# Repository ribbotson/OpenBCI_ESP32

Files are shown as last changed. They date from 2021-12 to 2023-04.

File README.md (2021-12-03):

# OpenBCI_ESP32
Clone of OpenBCI Brain Computer Interface Hardware using ESP32 Processor

>OpenBCI Cyton is a well performing Open source hardware and software design for a Brain Computer Interface. It was designed and developed over the last 7 years and used in many experimants and applications.
>This clone is designed because some of the parts used in the Cyton hardware are now obsolete and difficult to source. Also it is hoped that a new design can offer higher throughput. 
The design will continue to use the TI ADS1299 Analog Front end so perfomance should be the same as Cyton. The option to have either 8 or 16 channels will be retained.

## Changes for ESP Version

**Replace existing PIC32MX processor with ESP32 processor with integral WiFi and Bluetooth**

>The ESP32 was chosen because it has integral WiFi and bluetooth and so replaces the obsolete RFD22301 bluetooth module and the WiFi board. The ESP32 is better supported under Arduino environment than PIC and RFD device. Raspberry Pi Zero W was considered as it has more processing power, but was excluded due to much higher power consumption so not suitable for battery operation.

**The design is split into two plugable modules**

>The base module supports the Processor, Micro SD Card, Accelerometer, and Power Supplies. One or two input modules are the stacked below to add 8 or 16 electrode inputs. The first base module will use a prebuilt ESP32 DEVkit C module to make firmware development easier. A later version could place as smaller ESP32 module directly on the base module.

**Boards only have components on one side**

>To simplify construction the new boards only have components mounted on one side of the board. Both boards are 2 layer PCB.

**Some components are to allow use of more common generic devices**

>Use of more common generic components should help with procurement especially if using outsourced PCB Assembly

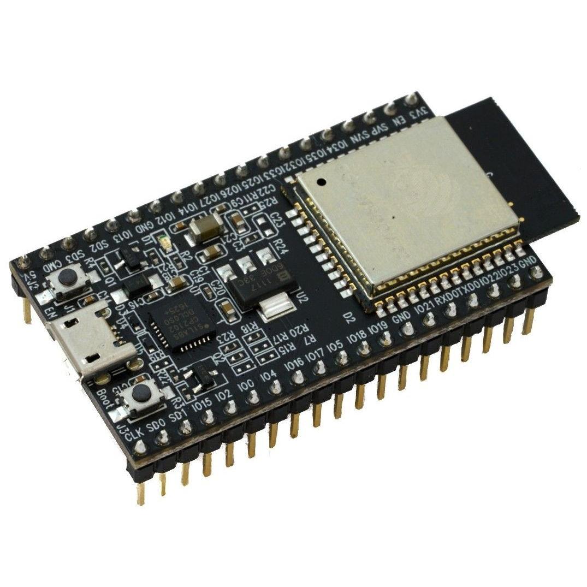
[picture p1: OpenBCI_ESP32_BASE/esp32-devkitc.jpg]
ESP32 DEVKIT C


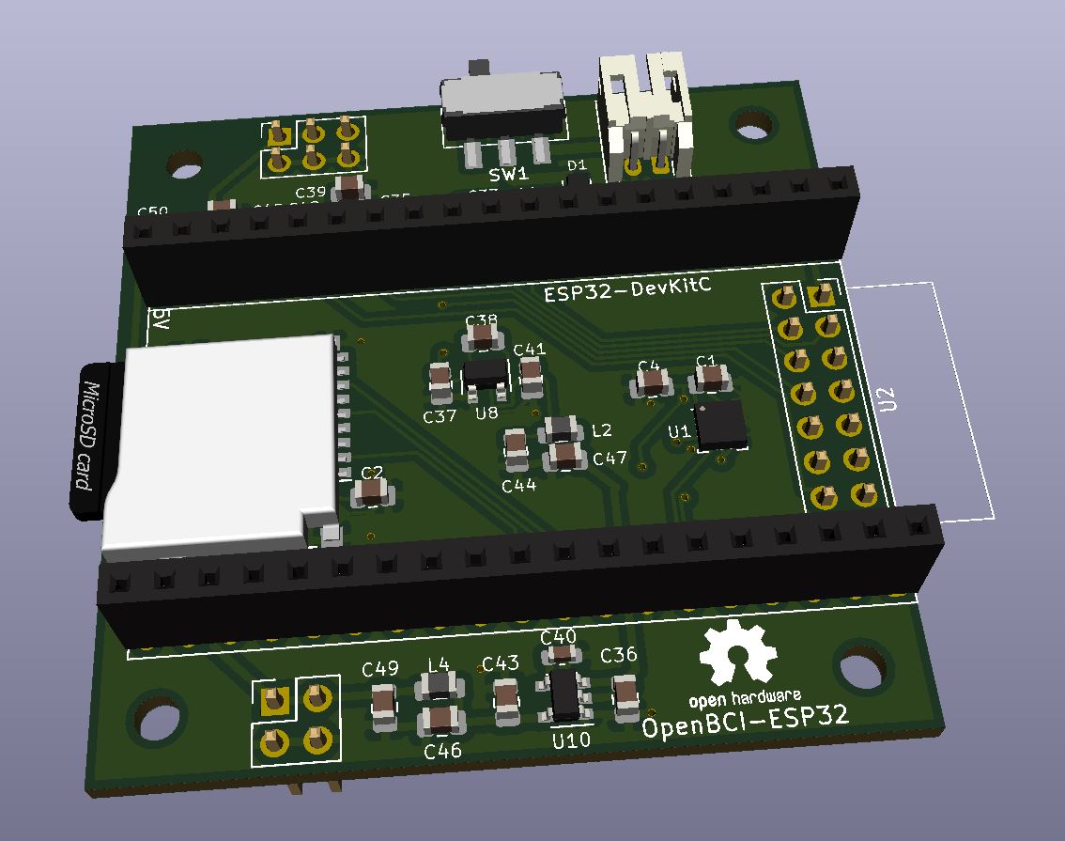
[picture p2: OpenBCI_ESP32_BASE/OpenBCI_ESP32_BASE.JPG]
OpenBCI ESP32 Base


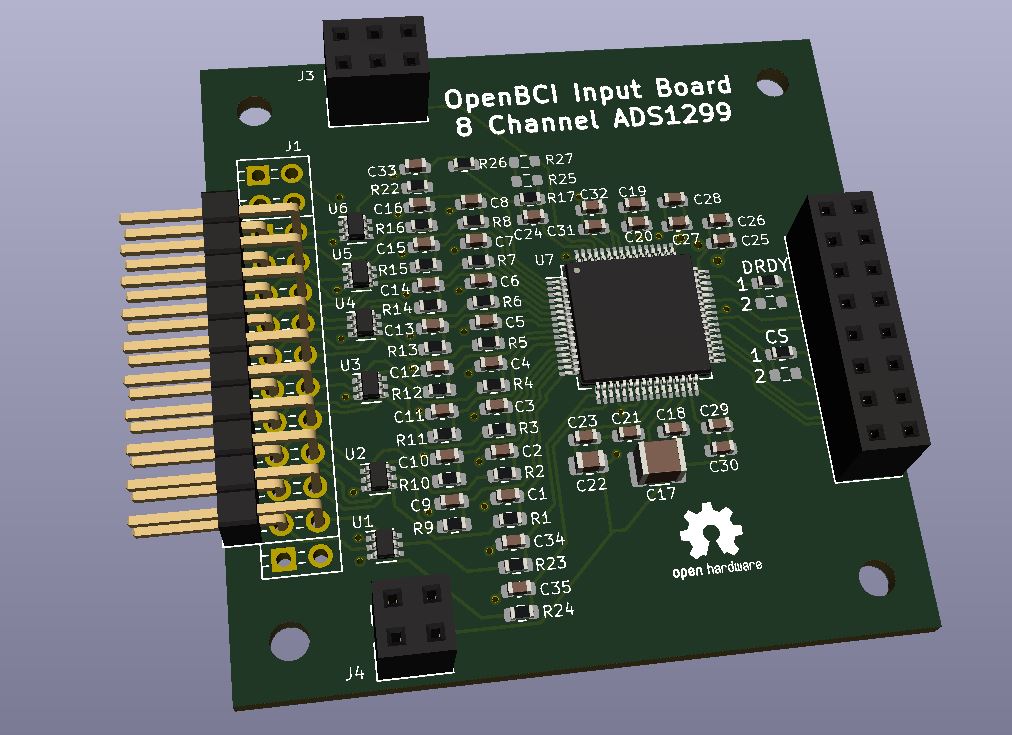
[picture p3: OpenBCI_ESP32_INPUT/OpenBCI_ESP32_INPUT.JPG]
OpenBCI ESP32 Input


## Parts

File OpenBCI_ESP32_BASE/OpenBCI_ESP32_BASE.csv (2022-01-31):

Source: | C:\Users\Richard Ibbotson\Documents\GitHub\OpenBCI_ESP32\OpenBCI_ESP32_BASE\OpenBCI_ESP32_BASE.kicad_sch
Date: | 27/01/2022 13:34
Tool: | Eeschema (6.0.1)
Generator: | C:\Program Files\KiCad\6.0\bin\scripting\plugins/bom_csv_grouped_by_value.py
Component Count: | 45
Individual Components:
Item | Qty | Reference(s) | Value | LibPart | Footprint | Datasheet | Manf | Manf#
 |  | C1 | 10u | Device:C | Capacitor_SMD:C_0805_2012Metric | ~
 |  | C2 | 10u | Device:C | Capacitor_SMD:C_0805_2012Metric | ~
 |  | C3 | 10u | Device:C | Capacitor_SMD:C_0805_2012Metric | ~
 |  | C4 | 0.1u | Device:C | Capacitor_SMD:C_0603_1608Metric | ~
 |  | C33 | 10u | Device:C | Capacitor_SMD:C_0805_2012Metric | ~
 |  | C34 | 10u | Device:C | Capacitor_SMD:C_0805_2012Metric | ~
 |  | C35 | 1u | Device:C | Capacitor_SMD:C_0603_1608Metric | ~
 |  | C36 | 2.2u | Device:C | Capacitor_SMD:C_0603_1608Metric | ~
 |  | C37 | 1u | Device:C | Capacitor_SMD:C_0603_1608Metric | ~
 |  | C38 | 1u | Device:C | Capacitor_SMD:C_0603_1608Metric | ~
 |  | C39 | 1u | Device:C | Capacitor_SMD:C_0603_1608Metric | ~
 |  | C40 | 10n | Device:C | Capacitor_SMD:C_0603_1608Metric | ~
 |  | C41 | 1u | Device:C | Capacitor_SMD:C_0603_1608Metric | ~
 |  | C42 | 2.2u | Device:C | Capacitor_SMD:C_0603_1608Metric | ~
 |  | C43 | 2.2u | Device:C | Capacitor_SMD:C_0603_1608Metric | ~
 |  | C44 | 10u | Device:C | Capacitor_SMD:C_0805_2012Metric | ~
 |  | C45 | 10u | Device:C | Capacitor_SMD:C_0805_2012Metric | ~
 |  | C46 | 10u | Device:C | Capacitor_SMD:C_0805_2012Metric | ~
 |  | C47 | 10u | Device:C | Capacitor_SMD:C_0805_2012Metric | ~
 |  | C48 | 10u | Device:C | Capacitor_SMD:C_0805_2012Metric | ~
 |  | C49 | 10u | Device:C | Capacitor_SMD:C_0805_2012Metric | ~
 |  | C50 | 0.1u | Device:C | Capacitor_SMD:C_0603_1608Metric | ~
 |  | D1 | D_Schottky | Device:D_Schottky | Diode_SMD:D_SOD-123 | ~
 |  | H1 | MountingHole | Mechanical:MountingHole | MountingHole:MountingHole_2.7mm_M2.5 | ~
 |  | H2 | MountingHole | Mechanical:MountingHole | MountingHole:MountingHole_2.7mm_M2.5 | ~
 |  | H3 | MountingHole | Mechanical:MountingHole | MountingHole:MountingHole_2.7mm_M2.5 | ~
 |  | H4 | MountingHole | Mechanical:MountingHole | MountingHole:MountingHole_2.7mm_M2.5 | ~
 |  | J1 | Conn_01x02 | Connector_Generic:Conn_01x02 | Connector_JST:JST_PH_S2B-PH-SM4-TB_1x02-1MP_P2.00mm_Horizontal | ~
 |  | J2 | Conn_02x03_Odd_Even | Connector_Generic:Conn_02x03_Odd_Even | OpenBCI_ESP32:PinHeaderReverse_2x03_P2.54mm_OpenBCI | ~
 |  | J3 | Conn_02x02_Odd_Even | Connector_Generic:Conn_02x02_Odd_Even | OpenBCI_ESP32:PinHeaderReverse_2x02_P2.54mml_OpenBCI | ~
 |  | J4 | Conn_02x08_Odd_Even | Connector_Generic:Conn_02x08_Odd_Even | OpenBCI_ESP32:PinHeaderReverse_2x08_P2.54mm_OpenBCI | ~
 |  | L1 | 3.3u | Device:L | Inductor_SMD:L_0805_2012Metric | ~
 |  | L2 | 3.3u | Device:L | Inductor_SMD:L_0805_2012Metric | ~
 |  | L3 | 3.3u | Device:L | Inductor_SMD:L_0805_2012Metric | ~
 |  | L4 | 3.3u | Device:L | Inductor_SMD:L_0805_2012Metric | ~
 |  | LOGO1 | Logo_Open_Hardware_Small | Graphic:Logo_Open_Hardware_Small | Symbol:OSHW-Logo2_7.3x6mm_SilkScreen | ~
 |  | R1 | NF | Device:R | Resistor_SMD:R_0603_1608Metric | ~
 |  | R2 | NF | Device:R | Resistor_SMD:R_0603_1608Metric | ~
 |  | SW1 | SW_SPDT | Switch:SW_SPDT | Button_Switch_SMD:SW_SPDT_CK-JS102011SAQN | ~
 |  | U1 | LIS3DH | Sensor_Motion:LIS3DH | Package_LGA:LGA-16_3x3mm_P0.5mm_LayoutBorder3x5y | https://www.st.com/resource/en/datasheet/cd00274221.pdf
 |  | U2 | ESP32-DevKitC | Espressif:ESP32-DevKitC | OpenBCI_ESP32:ESP32-DevKitC | https://docs.espressif.com/projects/esp-idf/zh_CN/latest/esp32/hw-reference/esp32/get-started-devkitc.html
 |  | U8 | TPS60403 | OpenBCI_ESP32:TPS60403 | Package_TO_SOT_SMD:SOT-23-5
 |  | U9 | TPS73225 | OpenBCI_ESP32:TPS73225 | Package_TO_SOT_SMD:SOT-23-5
 |  | U10 | TPS72325 | OpenBCI_ESP32:TPS72325 | Package_TO_SOT_SMD:SOT-23-5
 |  | XS1 | SD_ebay-uSD-push_push_SMD | uSD_Socket:SD_ebay-uSD-push_push_SMD | OpenBCI_ESP32:Conn_uSDcard | _ | ebay | _
Collated Components:
Item | Qty | Reference(s) | Value | LibPart | Footprint | Datasheet | Manf | Manf#
1 | 11 | C1, C2, C3, C33, C34, C44, C45, C46, C47, C48, C49 | 10u | Device:C | Capacitor_SMD:C_0805_2012Metric | ~
2 | 2 | C4, C50 | 0.1u | Device:C | Capacitor_SMD:C_0603_1608Metric | ~
3 | 5 | C35, C37, C38, C39, C41 | 1u | Device:C | Capacitor_SMD:C_0603_1608Metric | ~
4 | 3 | C36, C42, C43 | 2.2u | Device:C | Capacitor_SMD:C_0603_1608Metric | ~
5 | 1 | C40 | 10n | Device:C | Capacitor_SMD:C_0603_1608Metric | ~
6 | 1 | D1 | D_Schottky | Device:D_Schottky | Diode_SMD:D_SOD-123 | ~
7 | 4 | H1, H2, H3, H4 | MountingHole | Mechanical:MountingHole | MountingHole:MountingHole_2.7mm_M2.5 | ~
8 | 1 | J1 | Conn_01x02 | Connector_Generic:Conn_01x02 | Connector_JST:JST_PH_S2B-PH-SM4-TB_1x02-1MP_P2.00mm_Horizontal | ~
9 | 1 | J2 | Conn_02x03_Odd_Even | Connector_Generic:Conn_02x03_Odd_Even | OpenBCI_ESP32:PinHeaderReverse_2x03_P2.54mm_OpenBCI | ~
10 | 1 | J3 | Conn_02x02_Odd_Even | Connector_Generic:Conn_02x02_Odd_Even | OpenBCI_ESP32:PinHeaderReverse_2x02_P2.54mml_OpenBCI | ~
11 | 1 | J4 | Conn_02x08_Odd_Even | Connector_Generic:Conn_02x08_Odd_Even | OpenBCI_ESP32:PinHeaderReverse_2x08_P2.54mm_OpenBCI | ~
12 | 4 | L1, L2, L3, L4 | 3.3u | Device:L | Inductor_SMD:L_0805_2012Metric | ~
13 | 1 | LOGO1 | Logo_Open_Hardware_Small | Graphic:Logo_Open_Hardware_Small | Symbol:OSHW-Logo2_7.3x6mm_SilkScreen | ~
14 | 2 | R1, R2 | NF | Device:R | Resistor_SMD:R_0603_1608Metric | ~
15 | 1 | SW1 | SW_SPDT | Switch:SW_SPDT | Button_Switch_SMD:SW_SPDT_CK-JS102011SAQN | ~
16 | 1 | U1 | LIS3DH | Sensor_Motion:LIS3DH | Package_LGA:LGA-16_3x3mm_P0.5mm_LayoutBorder3x5y | https://www.st.com/resource/en/datasheet/cd00274221.pdf
17 | 1 | U2 | ESP32-DevKitC | Espressif:ESP32-DevKitC | OpenBCI_ESP32:ESP32-DevKitC | https://docs.espressif.com/projects/esp-idf/zh_CN/latest/esp32/hw-reference/esp32/get-started-devkitc.html
18 | 1 | U8 | TPS60403 | OpenBCI_ESP32:TPS60403 | Package_TO_SOT_SMD:SOT-23-5
19 | 1 | U9 | TPS73225 | OpenBCI_ESP32:TPS73225 | Package_TO_SOT_SMD:SOT-23-5
20 | 1 | U10 | TPS72325 | OpenBCI_ESP32:TPS72325 | Package_TO_SOT_SMD:SOT-23-5
21 | 1 | XS1 | SD_ebay-uSD-push_push_SMD | uSD_Socket:SD_ebay-uSD-push_push_SMD | OpenBCI_ESP32:Conn_uSDcard | _ | ebay | _

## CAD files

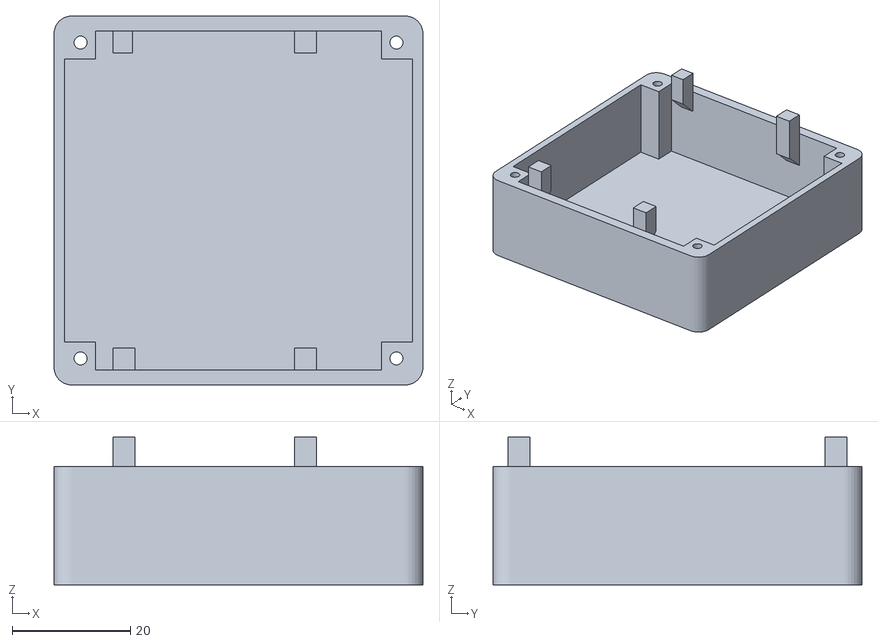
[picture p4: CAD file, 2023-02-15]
Case/Battery.stl
62.5 x 62.5 x 25.0

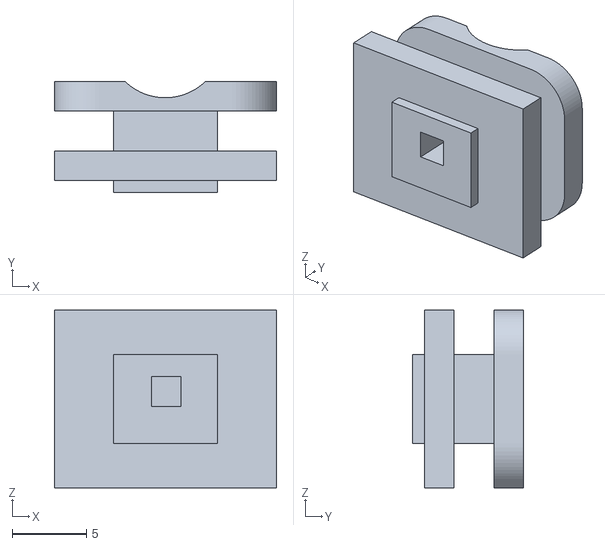
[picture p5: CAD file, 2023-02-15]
Case/Switch.stl
15.0 x 7.50 x 12.0

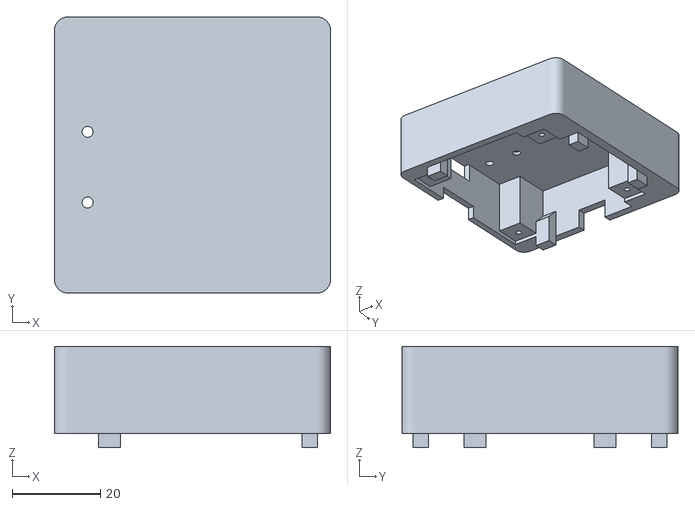
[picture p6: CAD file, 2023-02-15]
Case/Base.stl
62.5 x 62.5 x 22.9

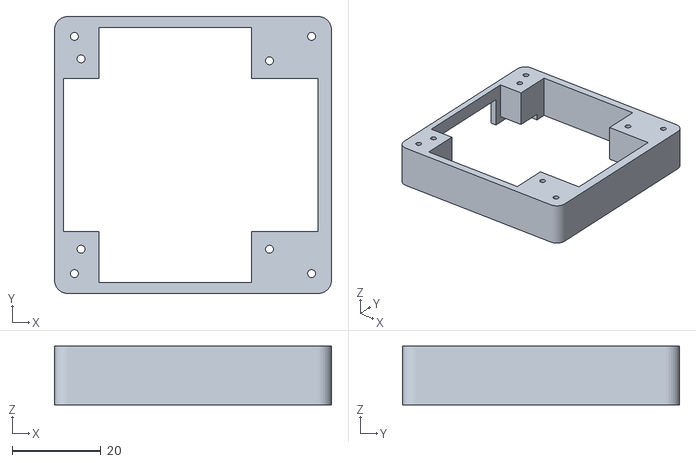
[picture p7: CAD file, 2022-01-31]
Case/Input_8.stl
62.5 x 62.5 x 13.2

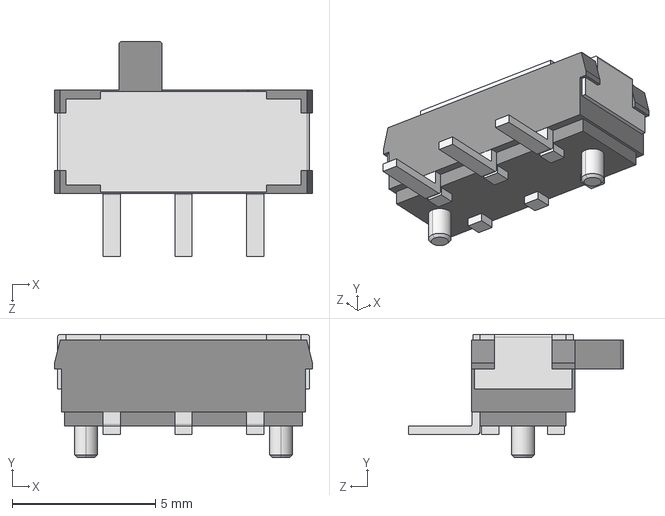
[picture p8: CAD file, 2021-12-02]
OpenBCI_ESP32_BASE/JS102011SAQN.STEP
9.00 x 4.30 x 7.50 mm

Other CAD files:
Case/OpenBCI_ESP v11.f3d

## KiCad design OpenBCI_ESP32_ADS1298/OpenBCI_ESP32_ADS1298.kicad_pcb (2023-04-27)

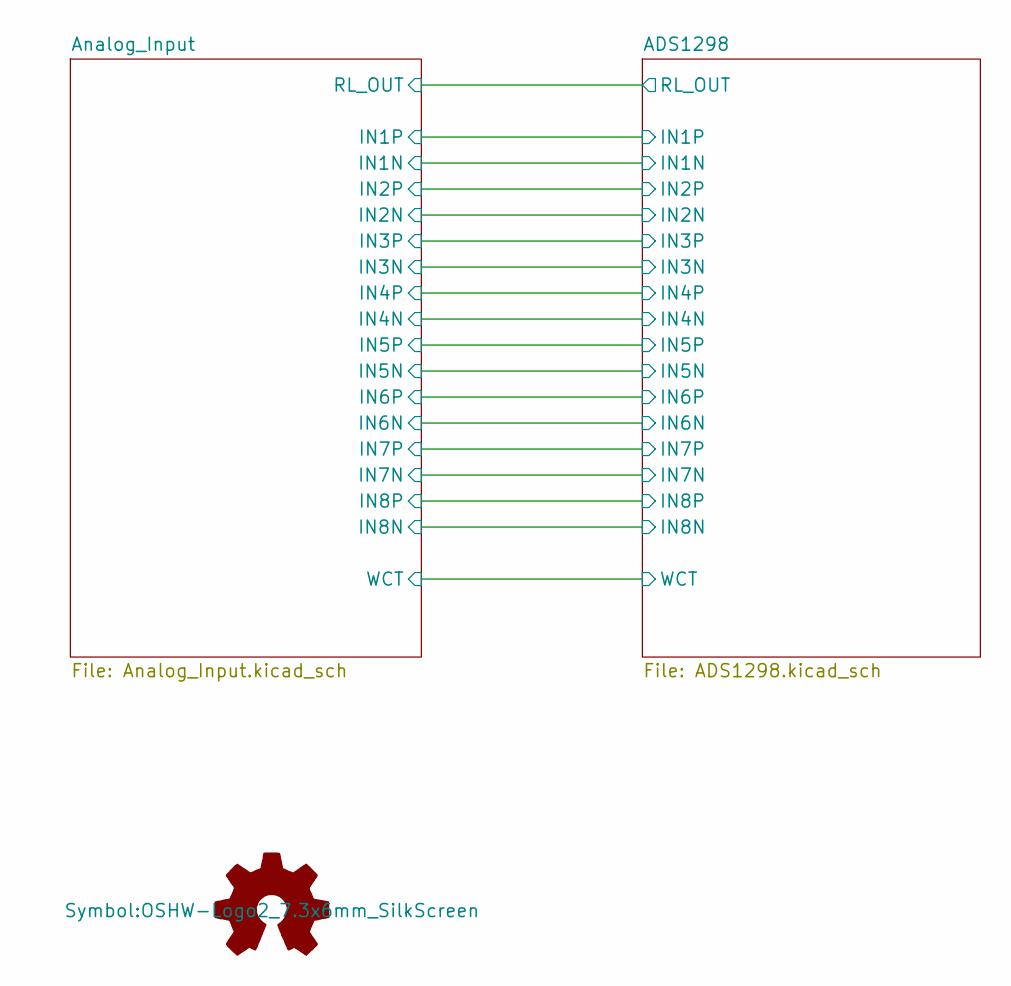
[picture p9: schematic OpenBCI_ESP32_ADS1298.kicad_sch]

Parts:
LOGO1: Logo_Open_Hardware_Small; OSHW-Logo2_7.3x6mm_SilkScreen

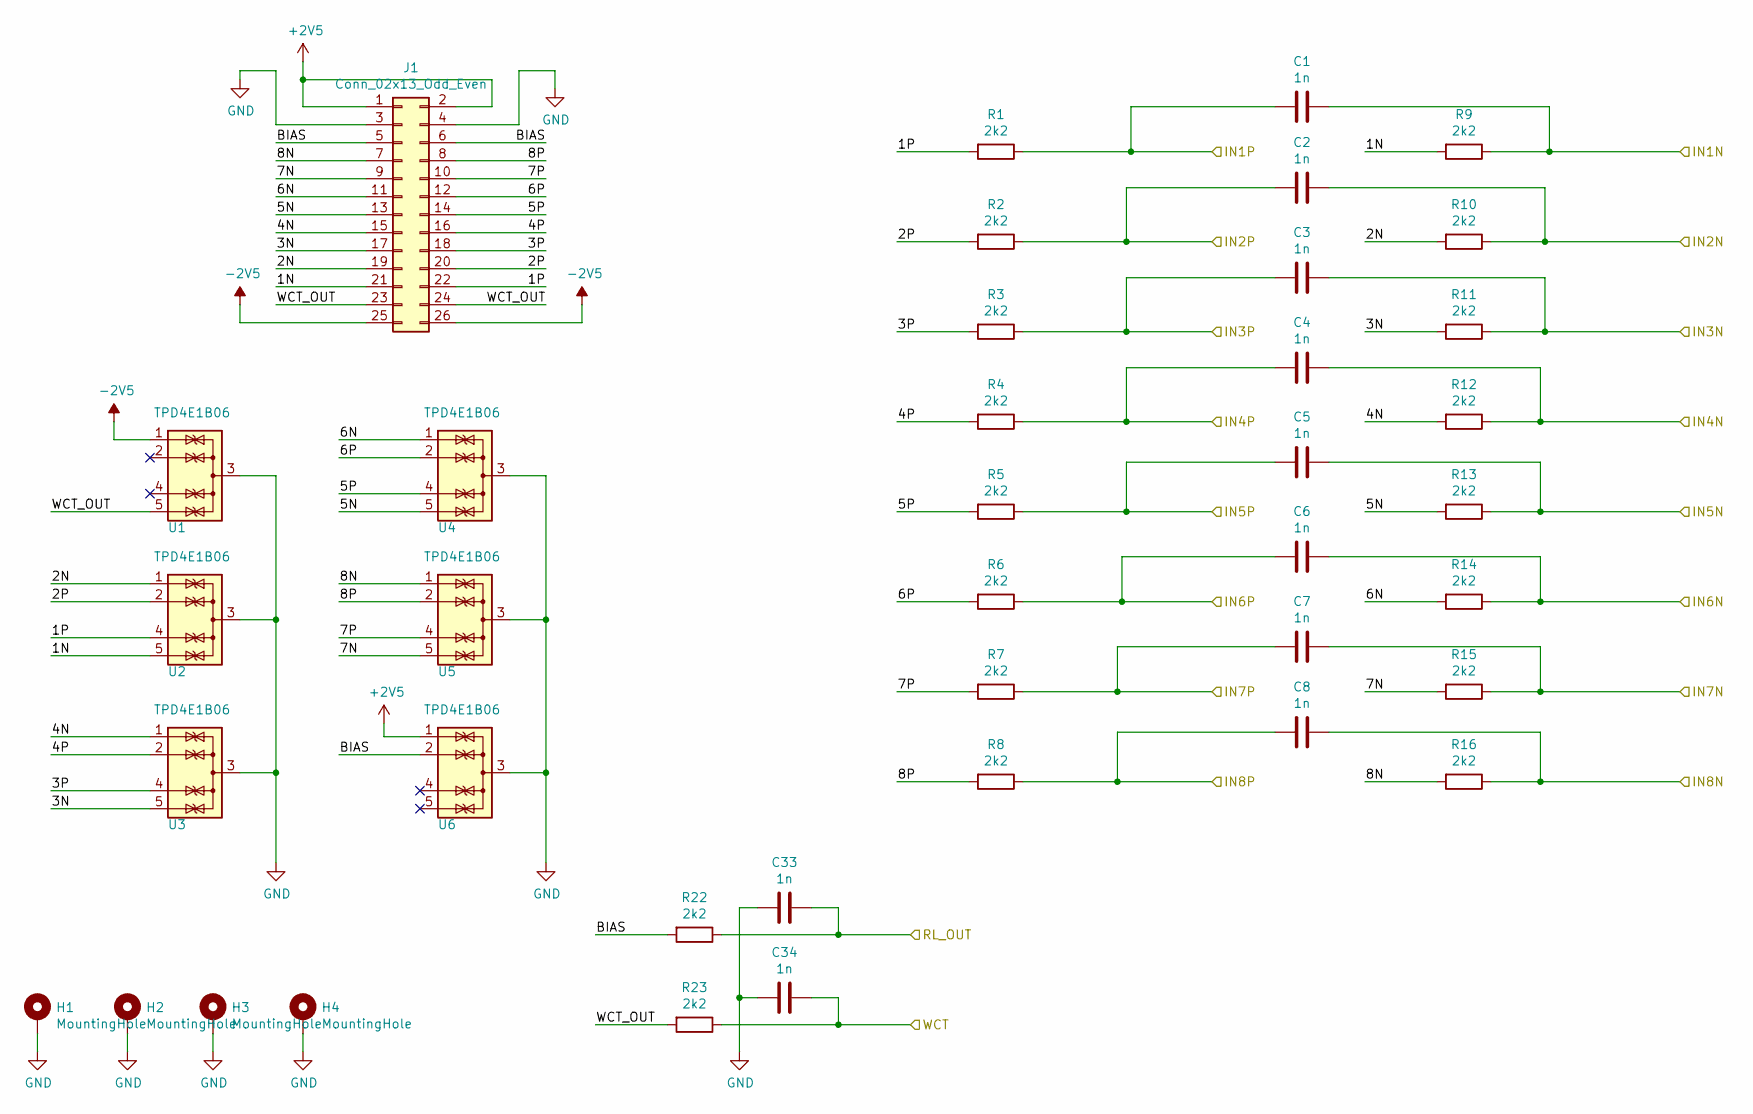
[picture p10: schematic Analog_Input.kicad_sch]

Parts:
C1, C2, C3, C4, C5, C6, C7, C8, C33, C34: 1n; C_0603_1608Metric
H1, H2, H3, H4: MountingHole; MountingHole_2.7mm_M2.5_DIN965_Pad_TopBottom
J1: Conn_02x13_Odd_Even; PinHeader_2x13_P2.54mm_OpenBCI
R1, R2, R3, R4, R5, R6, R7, R8, R9, R10, R11, R12, R13, R14, R15, R16, R22, R23: 2k2; R_0603_1608Metric
U1, U2, U3, U4, U5, U6: TPD4E1B06; SOT-363_SC-70-6

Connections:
+2V5: J1.1, J1.2, U6.1 (IO1); also elsewhere on the board
-2V5: J1.25, J1.26, U1.1 (IO1); also elsewhere on the board
/ADS1298/IN1N: C1.1, R9.1; also elsewhere on the board
/ADS1298/IN1P: C1.2, R1.1; also elsewhere on the board
/ADS1298/IN2N: C2.1, R10.1; also elsewhere on the board
/ADS1298/IN2P: C2.2, R2.1; also elsewhere on the board
/ADS1298/IN3N: C3.1, R11.1; also elsewhere on the board
/ADS1298/IN3P: C3.2, R3.1; also elsewhere on the board
/ADS1298/IN4N: C4.1, R12.1; also elsewhere on the board
/ADS1298/IN4P: C4.2, R4.1; also elsewhere on the board
/ADS1298/IN5N: C5.1, R13.1; also elsewhere on the board
/ADS1298/IN5P: C5.2, R5.1; also elsewhere on the board
/ADS1298/IN6N: C6.1, R14.1; also elsewhere on the board
/ADS1298/IN6P: C6.2, R6.1; also elsewhere on the board
/ADS1298/IN7N: C7.1, R15.1; also elsewhere on the board
/ADS1298/IN7P: C7.2, R7.1; also elsewhere on the board
/ADS1298/IN8N: C8.1, R16.1; also elsewhere on the board
/ADS1298/IN8P: C8.2, R8.1; also elsewhere on the board
/ADS1298/RL_OUT: C33.1, R22.1; also elsewhere on the board
/ADS1298/WCT: C34.1, R23.1; also elsewhere on the board
/Analog_Input/1N: J1.21, R9.2, U2.5 (IO4)
/Analog_Input/1P: J1.22, R1.2, U2.4 (IO3)
/Analog_Input/2N: J1.19, R10.2, U2.1 (IO1)
/Analog_Input/2P: J1.20, R2.2, U2.2 (IO2)
/Analog_Input/3N: J1.17, R11.2, U3.5 (IO4)
/Analog_Input/3P: J1.18, R3.2, U3.4 (IO3)
/Analog_Input/4N: J1.15, R12.2, U3.1 (IO1)
/Analog_Input/4P: J1.16, R4.2, U3.2 (IO2)
/Analog_Input/5N: J1.13, R13.2, U4.5 (IO4)
/Analog_Input/5P: J1.14, R5.2, U4.4 (IO3)
/Analog_Input/6N: J1.11, R14.2, U4.1 (IO1)
/Analog_Input/6P: J1.12, R6.2, U4.2 (IO2)
/Analog_Input/7N: J1.9, R15.2, U5.5 (IO4)
/Analog_Input/7P: J1.10, R7.2, U5.4 (IO3)
/Analog_Input/8N: J1.7, R16.2, U5.1 (IO1)
/Analog_Input/8P: J1.8, R8.2, U5.2 (IO2)
/Analog_Input/BIAS: J1.5, J1.6, R22.2, U6.2 (IO2)
/Analog_Input/WCT_OUT: J1.23, J1.24, R23.2, U1.5 (IO4)
GND: C33.2, C34.2, H1.1, H2.1, H3.1, H4.1, J1.3, J1.4, U1.3 (G), U2.3 (G), U3.3 (G), U4.3 (G), U5.3 (G), U6.3 (G); also elsewhere on the board

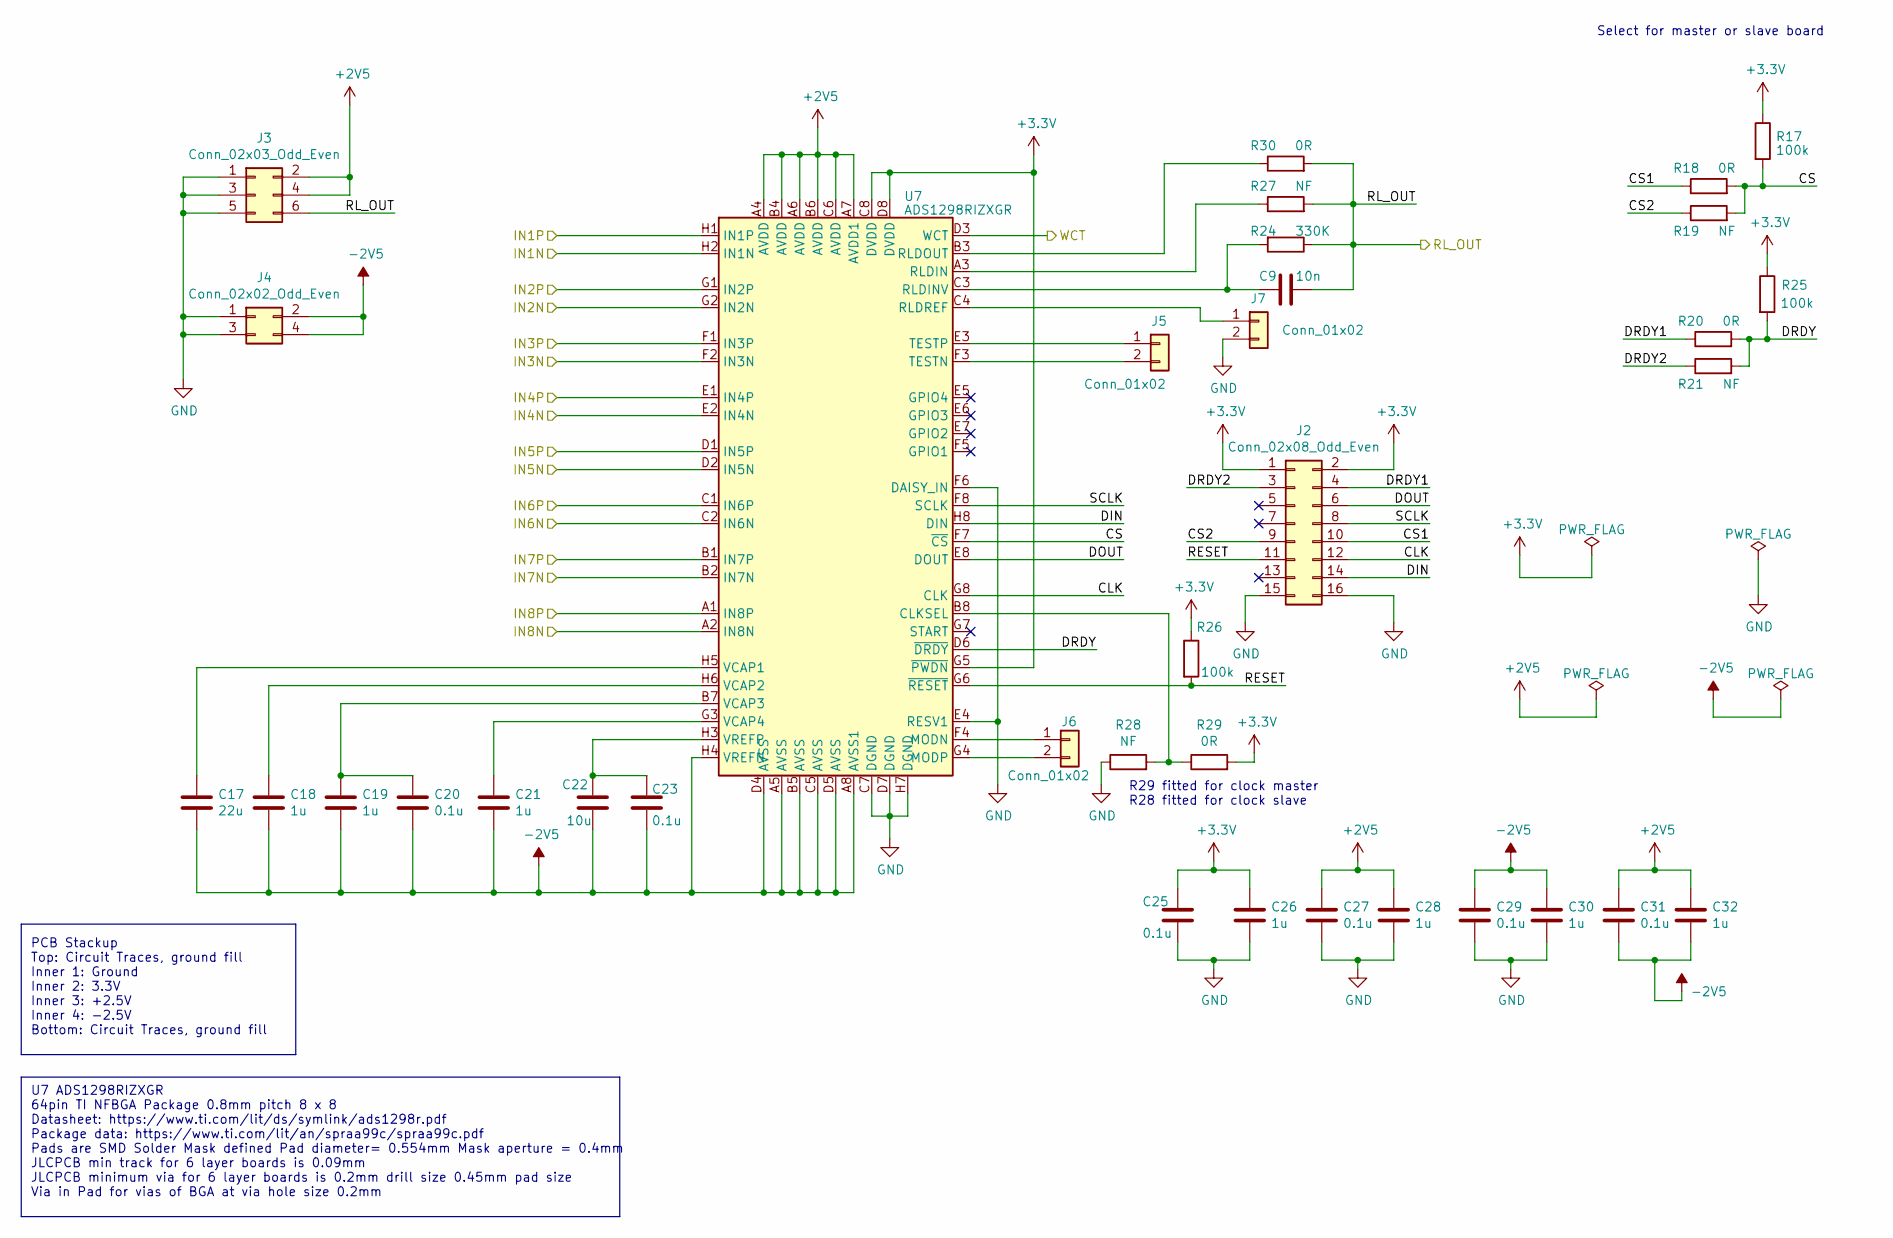
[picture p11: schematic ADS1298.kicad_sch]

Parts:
C9: 10n; C_0603_1608Metric
C17: 22u; C_0805_2012Metric
C18, C19, C21, C26, C28, C30, C32: 1u; C_0603_1608Metric
C20, C23, C25, C27, C29, C31: 0.1u; C_0603_1608Metric
C22: 10u; C_0805_2012Metric
J2: Conn_02x08_Odd_Even; PinSocket_2x08_P2.54mm_Vertical
J3: Conn_02x03_Odd_Even; PinSocket_2x03_P2.54mm_Vertical
J4: Conn_02x02_Odd_Even; PinSocket_2x02_P2.54mm_Vertical
J5, J6, J7: Conn_01x02; PinHeader_1x02_P2.00mm_Vertical
R17, R25, R26: 100k; R_0603_1608Metric
R18, R20, R29, R30: 0R; R_0603_1608Metric
R19, R21, R27, R28: NF; R_0603_1608Metric
R24: 330K; R_0603_1608Metric
U7: ADS1298RIZXGR; BGA-64_8x8_8.0x8.0mm

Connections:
+2V5: C27.1, C28.1, C31.1, C32.1, J3.2, J3.4, U7.A4 (AVDD), U7.A6 (AVDD), U7.A7 (AVDD1), U7.B4 (AVDD), U7.B6 (AVDD), U7.C6 (AVDD); also elsewhere on the board
+3.3V: C25.1, C26.1, J2.1, J2.2, R17.1, R25.1, R26.1, R29.2, U7.C8 (DVDD), U7.D8 (DVDD), U7.G5 (~PWDN)
-2V5: C17.2, C18.2, C19.2, C20.2, C21.2, C22.2, C23.2, C29.1, C30.1, C31.2, C32.2, J4.2, J4.4, U7.A5 (AVSS), U7.A8 (AVSS1), U7.B5 (AVSS), U7.C5 (AVSS), U7.D4 (AVSS), U7.D5 (AVSS), U7.H4 (VREFN); also elsewhere on the board
/ADS1298/CLK: J2.12, U7.G8 (CLK)
/ADS1298/CS: R17.2, R18.2, R19.2, U7.F7 (~CS)
/ADS1298/CS1: J2.10, R18.1
/ADS1298/CS2: J2.9, R19.1
/ADS1298/DIN: J2.14, U7.H8 (DIN)
/ADS1298/DOUT: J2.6, U7.E8 (DOUT)
/ADS1298/DRDY: R20.2, R21.2, R25.2, U7.D6 (~DRDY)
/ADS1298/DRDY1: J2.4, R20.1
/ADS1298/DRDY2: J2.3, R21.1
/ADS1298/IN1N: U7.H2 (IN1N); also elsewhere on the board
/ADS1298/IN1P: U7.H1 (IN1P); also elsewhere on the board
/ADS1298/IN2N: U7.G2 (IN2N); also elsewhere on the board
/ADS1298/IN2P: U7.G1 (IN2P); also elsewhere on the board
/ADS1298/IN3N: U7.F2 (IN3N); also elsewhere on the board
/ADS1298/IN3P: U7.F1 (IN3P); also elsewhere on the board
/ADS1298/IN4N: U7.E2 (IN4N); also elsewhere on the board
/ADS1298/IN4P: U7.E1 (IN4P); also elsewhere on the board
/ADS1298/IN5N: U7.D2 (IN5N); also elsewhere on the board
/ADS1298/IN5P: U7.D1 (IN5P); also elsewhere on the board
/ADS1298/IN6N: U7.C2 (IN6N); also elsewhere on the board
/ADS1298/IN6P: U7.C1 (IN6P); also elsewhere on the board
/ADS1298/IN7N: U7.B2 (IN7N); also elsewhere on the board
/ADS1298/IN7P: U7.B1 (IN7P); also elsewhere on the board
/ADS1298/IN8N: U7.A2 (IN8N); also elsewhere on the board
/ADS1298/IN8P: U7.A1 (IN8P); also elsewhere on the board
/ADS1298/RESET: J2.11, R26.2, U7.G6 (~RESET)
/ADS1298/RL_OUT: C9.2, J3.6, R24.1, R27.2, R30.2; also elsewhere on the board
/ADS1298/SCLK: J2.8, U7.F8 (SCLK)
/ADS1298/WCT: U7.D3 (WCT); also elsewhere on the board
GND: C25.2, C26.2, C27.2, C28.2, C29.2, C30.2, J2.15, J2.16, J3.1, J3.3, J3.5, J4.1, J4.3, J7.2, R28.1, U7.C7 (DGND), U7.D7 (DGND), U7.E4 (RESV1), U7.F6 (DAISY_IN), U7.H7 (DGND); also elsewhere on the board
unnamed: J5.1, U7.E3 (TESTP)
unnamed: J5.2, U7.F3 (TESTN)
unnamed: J6.1, U7.F4 (MODN)
unnamed: J6.2, U7.G4 (MODP)
unnamed: J7.1, U7.C4 (RLDREF)
unnamed: R28.2, R29.1, U7.B8 (CLKSEL)
unnamed: R27.1, U7.A3 (RLDIN)
unnamed: C9.1, R24.2, U7.C3 (RLDINV)
unnamed: R30.1, U7.B3 (RLDOUT)
unnamed: C17.1, U7.H5 (VCAP1)
unnamed: C18.1, U7.H6 (VCAP2)
unnamed: C19.1, C20.1, U7.B7 (VCAP3)
unnamed: C21.1, U7.G3 (VCAP4)
unnamed: C22.1, C23.1, U7.H3 (VREFP)

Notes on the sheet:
R29 fitted for clock master R28 fitted for clock slave
Select for master or slave board
U7 ADS1298RIZXGR 64pin TI NFBGA Package 0.8mm pitch 8 x 8 Datasheet: https://www.ti.com/lit/ds/symlink/ads1298r.pdf Package data: https://www.ti.com/lit/an/spraa99c/spraa99c.pdf Pads are SMD Solder Mask defined Pad diameter= 0.554mm Mask aperture = 0.4mm JLCPCB min track for 6 layer boards is 0.09m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
PCB Stackup Top: Circuit Traces, ground fill Inner 1: Ground Inner 2: 3.3V Inner 3: +2.5V Inner 4: -2.5V Bottom: Circuit Traces, ground fill

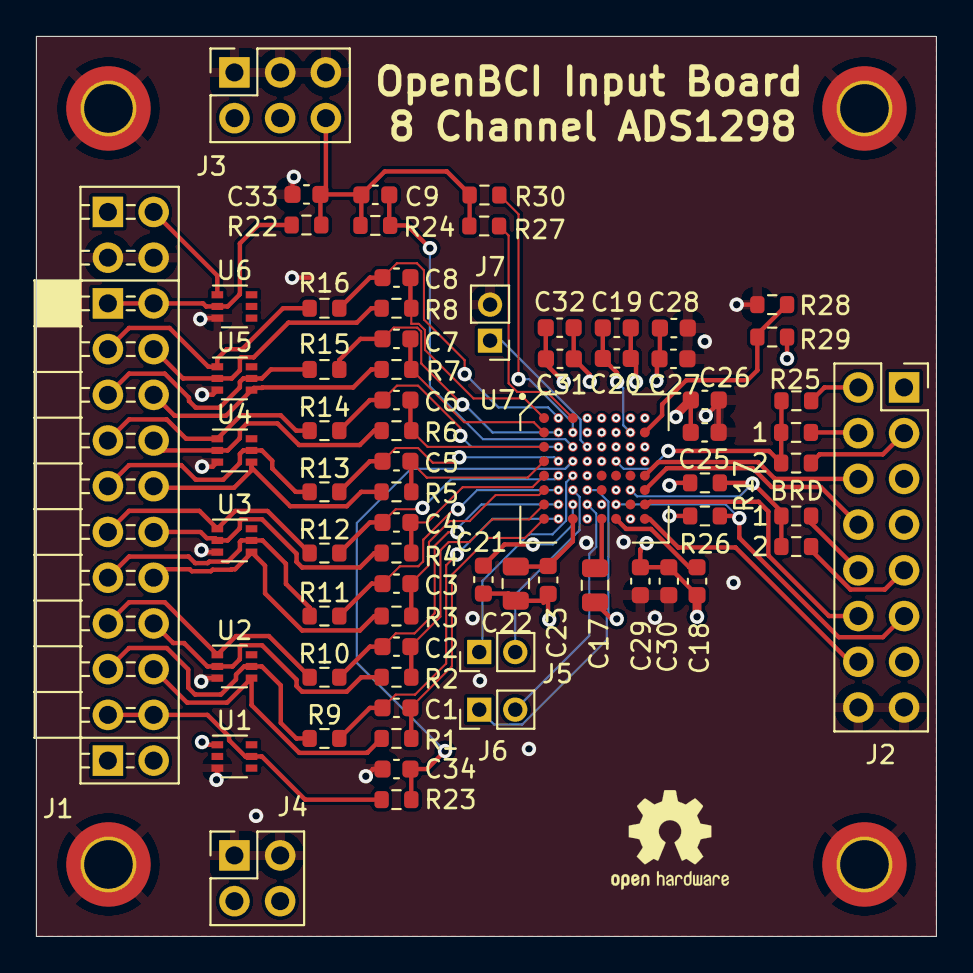
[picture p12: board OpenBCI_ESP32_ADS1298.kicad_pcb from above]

Board: 6 copper layers, 50.0 x 50.0 mm, 75 parts (0 on the bottom side), 65 nets.

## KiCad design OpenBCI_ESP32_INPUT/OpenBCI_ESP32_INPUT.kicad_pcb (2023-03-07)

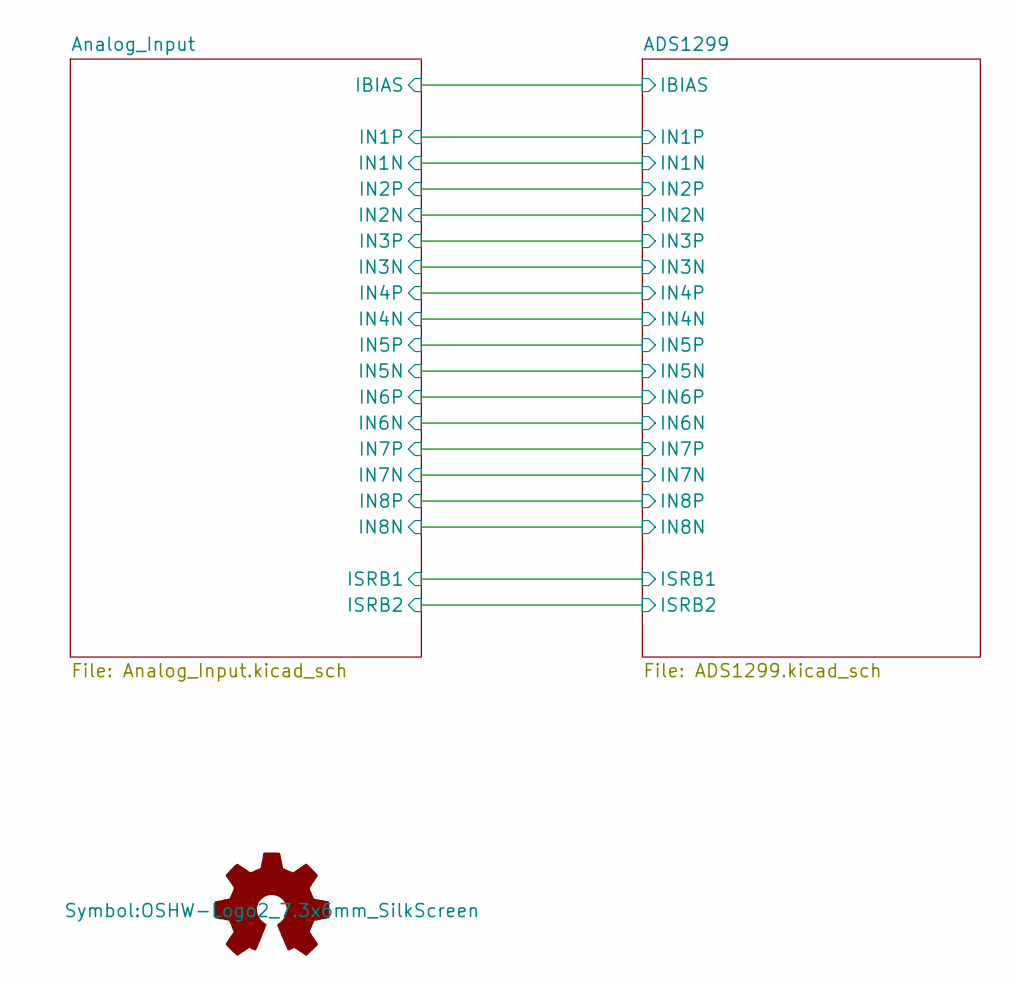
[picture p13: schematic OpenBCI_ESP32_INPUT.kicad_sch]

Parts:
LOGO1: Logo_Open_Hardware_Small; OSHW-Logo2_7.3x6mm_SilkScreen

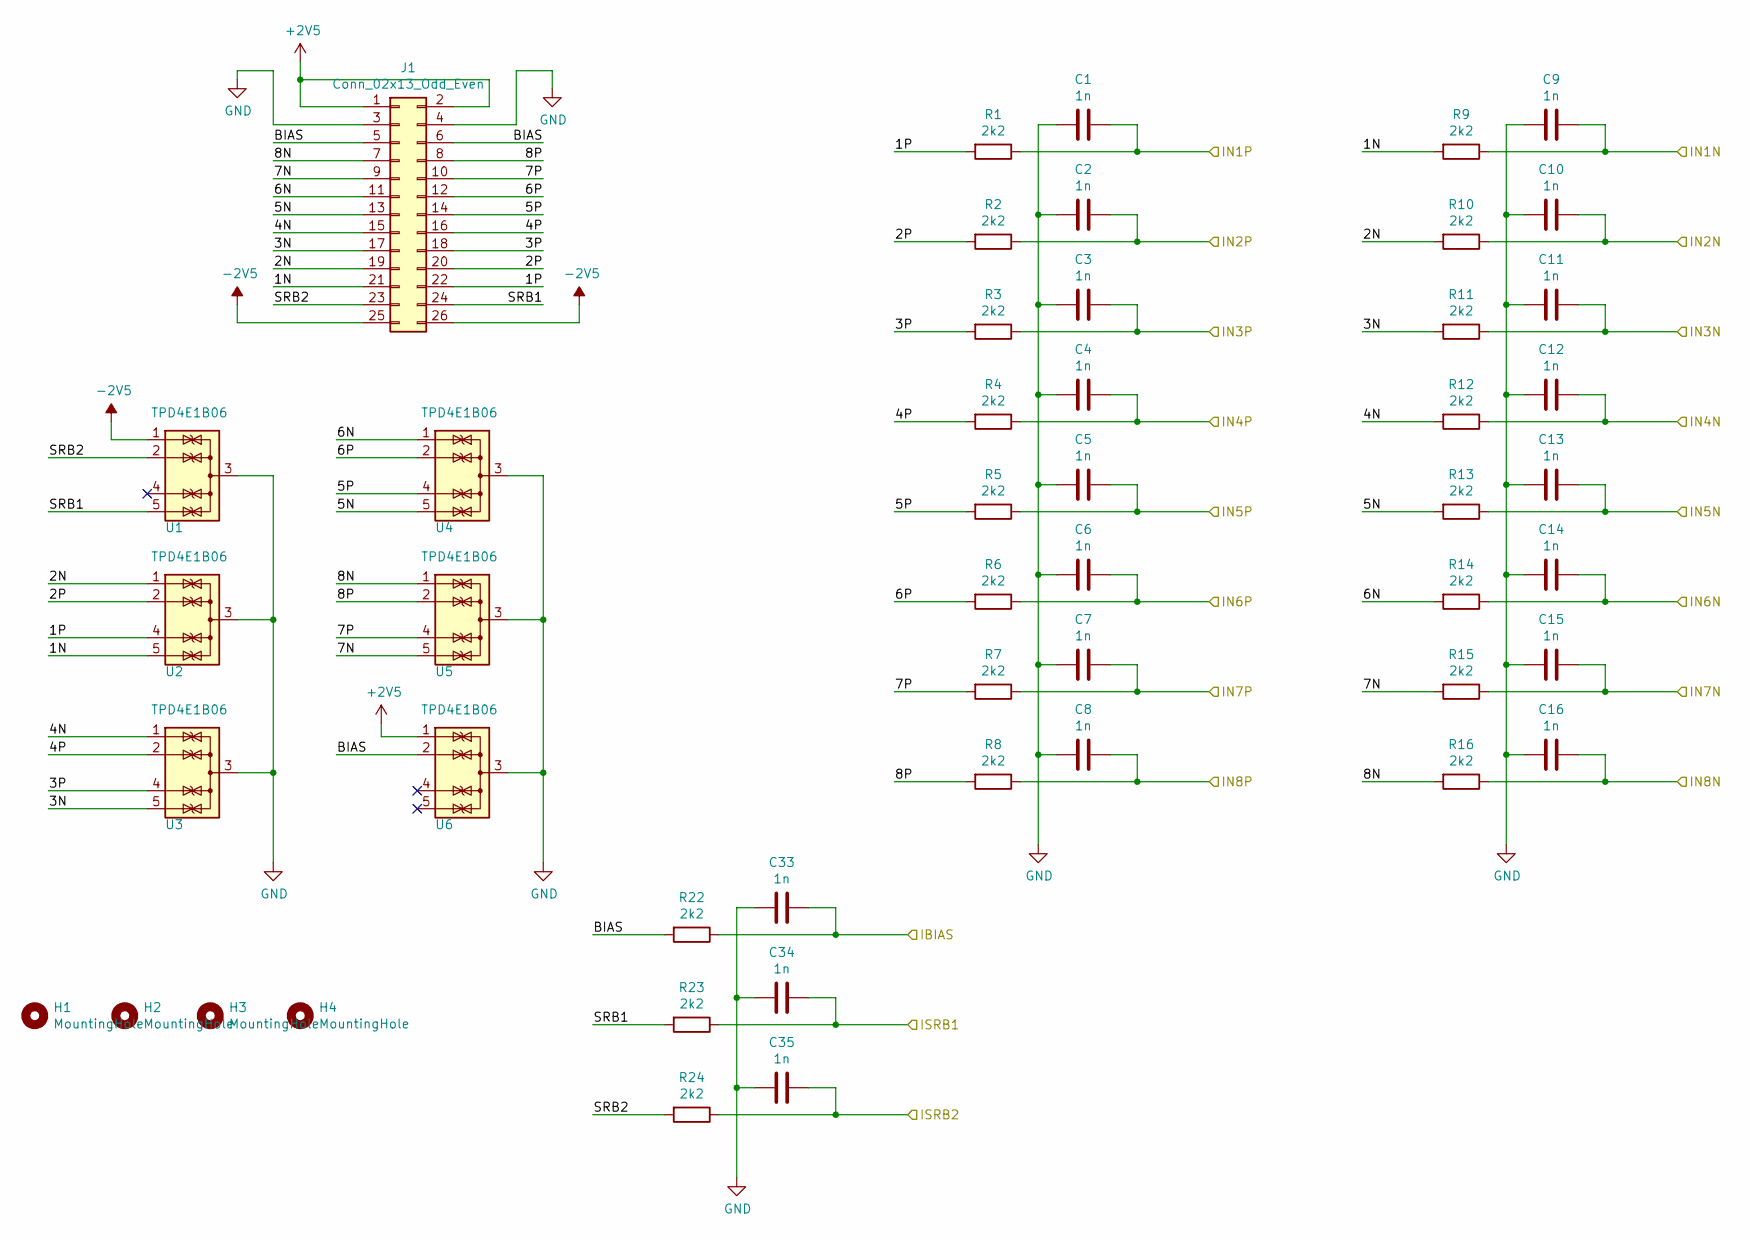
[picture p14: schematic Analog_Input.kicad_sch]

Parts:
C1, C2, C3, C4, C5, C6, C7, C8, C9, C10, C11, C12, C13, C14, C15, C16, C33, C34, C35: 1n; C_0603_1608Metric
H1, H2, H3, H4: MountingHole; MountingHole_2.7mm_M2.5
J1: Conn_02x13_Odd_Even; PinHeader_2x13_P2.54mm_OpenBCI
R1, R2, R3, R4, R5, R6, R7, R8, R9, R10, R11, R12, R13, R14, R15, R16, R22, R23, R24: 2k2; R_0603_1608Metric
U1, U2, U3, U4, U5, U6: TPD4E1B06; SOT-363_SC-70-6

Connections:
+2V5: J1.1, J1.2, U6.1 (IO1); also elsewhere on the board
-2V5: J1.25, J1.26, U1.1 (IO1); also elsewhere on the board
/ADS1299/IBIAS: C33.1, R22.1; also elsewhere on the board
/ADS1299/IN1N: C9.1, R9.1; also elsewhere on the board
/ADS1299/IN1P: C1.1, R1.1; also elsewhere on the board
/ADS1299/IN2N: C10.1, R10.1; also elsewhere on the board
/ADS1299/IN2P: C2.1, R2.1; also elsewhere on the board
/ADS1299/IN3N: C11.1, R11.1; also elsewhere on the board
/ADS1299/IN3P: C3.1, R3.1; also elsewhere on the board
/ADS1299/IN4N: C12.1, R12.1; also elsewhere on the board
/ADS1299/IN4P: C4.1, R4.1; also elsewhere on the board
/ADS1299/IN5N: C13.1, R13.1; also elsewhere on the board
/ADS1299/IN5P: C5.1, R5.1; also elsewhere on the board
/ADS1299/IN6N: C14.1, R14.1; also elsewhere on the board
/ADS1299/IN6P: C6.1, R6.1; also elsewhere on the board
/ADS1299/IN7N: C15.1, R15.1; also elsewhere on the board
/ADS1299/IN7P: C7.1, R7.1; also elsewhere on the board
/ADS1299/IN8N: C16.1, R16.1; also elsewhere on the board
/ADS1299/IN8P: C8.1, R8.1; also elsewhere on the board
/ADS1299/ISRB1: C34.1, R23.1; also elsewhere on the board
/ADS1299/ISRB2: C35.1, R24.1; also elsewhere on the board
/Analog_Input/1N: J1.21, R9.2, U2.5 (IO4)
/Analog_Input/1P: J1.22, R1.2, U2.4 (IO3)
/Analog_Input/2N: J1.19, R10.2, U2.1 (IO1)
/Analog_Input/2P: J1.20, R2.2, U2.2 (IO2)
/Analog_Input/3N: J1.17, R11.2, U3.5 (IO4)
/Analog_Input/3P: J1.18, R3.2, U3.4 (IO3)
/Analog_Input/4N: J1.15, R12.2, U3.1 (IO1)
/Analog_Input/4P: J1.16, R4.2, U3.2 (IO2)
/Analog_Input/5N: J1.13, R13.2, U4.5 (IO4)
/Analog_Input/5P: J1.14, R5.2, U4.4 (IO3)
/Analog_Input/6N: J1.11, R14.2, U4.1 (IO1)
/Analog_Input/6P: J1.12, R6.2, U4.2 (IO2)
/Analog_Input/7N: J1.9, R15.2, U5.5 (IO4)
/Analog_Input/7P: J1.10, R7.2, U5.4 (IO3)
/Analog_Input/8N: J1.7, R16.2, U5.1 (IO1)
/Analog_Input/8P: J1.8, R8.2, U5.2 (IO2)
/Analog_Input/BIAS: J1.5, J1.6, R22.2, U6.2 (IO2)
/Analog_Input/SRB1: J1.24, R23.2, U1.5 (IO4)
/Analog_Input/SRB2: J1.23, R24.2, U1.2 (IO2)
GND: C1.2, C2.2, C3.2, C4.2, C5.2, C6.2, C7.2, C8.2, C9.2, C10.2, C11.2, C12.2, C13.2, C14.2, C15.2, C16.2, C33.2, C34.2, C35.2, J1.3, J1.4, U1.3 (G), U2.3 (G), U3.3 (G), U4.3 (G), U5.3 (G), U6.3 (G); also elsewhere on the board

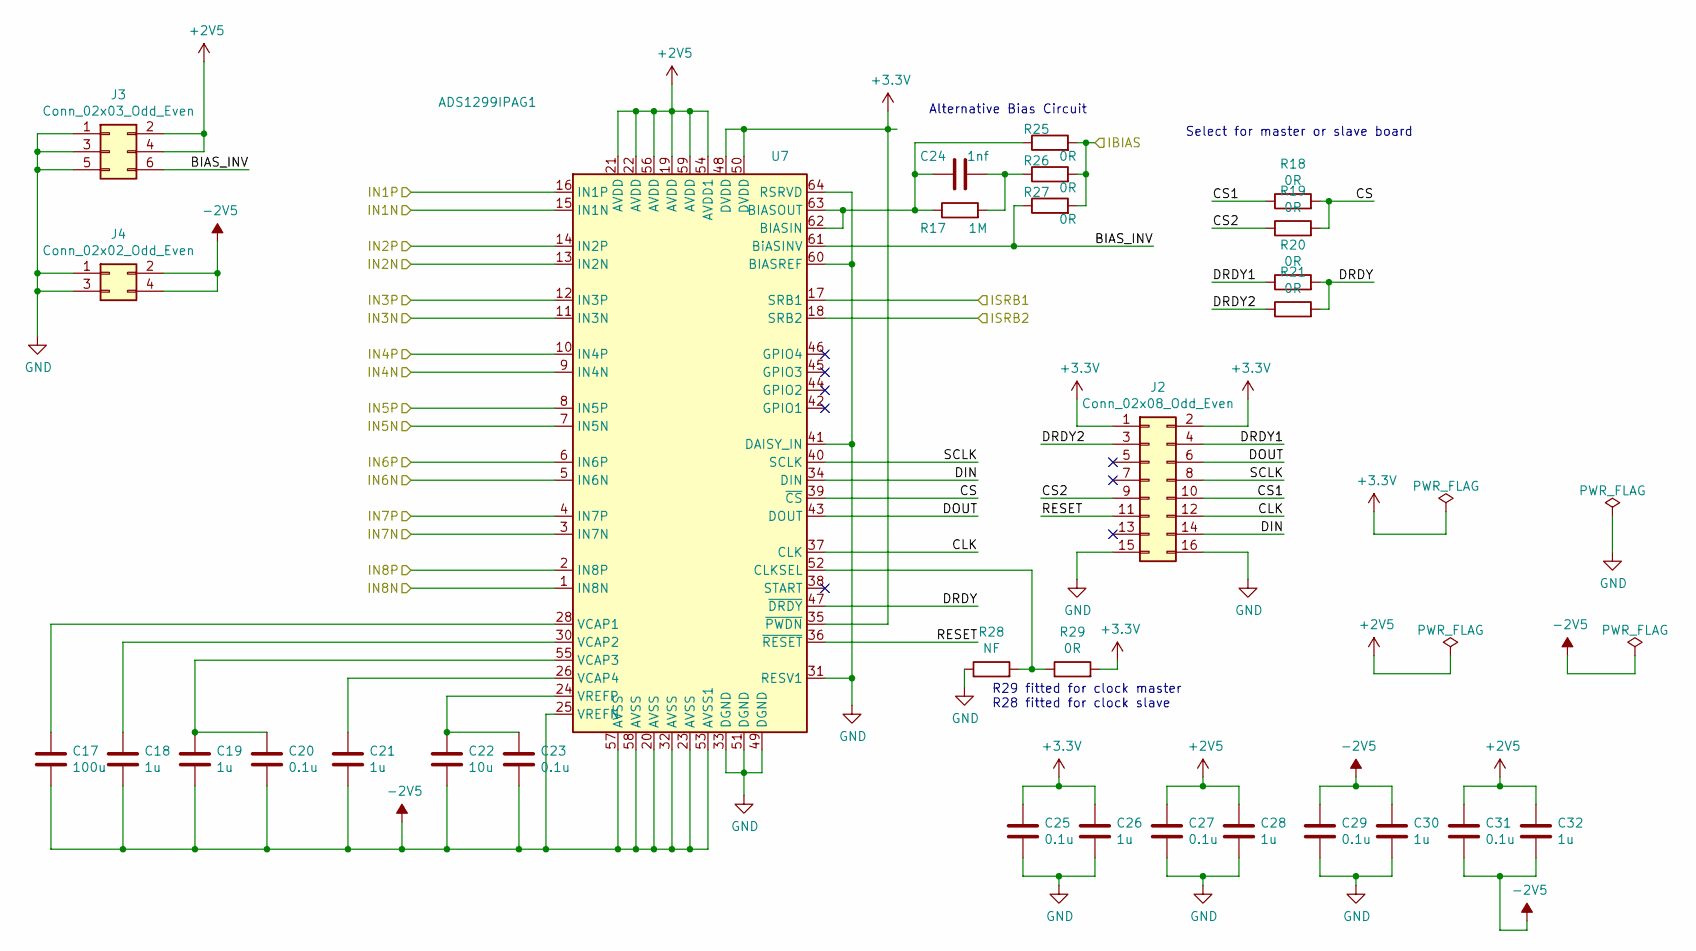
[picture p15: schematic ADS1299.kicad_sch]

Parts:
C17: 100u; C_1210_3225Metric
C18, C19, C21, C26, C28, C30, C32: 1u; C_0603_1608Metric
C20, C23, C25, C27, C29, C31: 0.1u; C_0603_1608Metric
C22: 10u; C_0805_2012Metric
C24: 1nf; C_0603_1608Metric
J2: Conn_02x08_Odd_Even; PinSocket_2x08_P2.54mm_Vertical
J3: Conn_02x03_Odd_Even; PinSocket_2x03_P2.54mm_Vertical
J4: Conn_02x02_Odd_Even; PinSocket_2x02_P2.54mm_Vertical
R17: 1M; R_0603_1608Metric
R18, R19, R20, R21, R25, R26, R27, R29: 0R; R_0603_1608Metric
R28: NF; R_0603_1608Metric
U7: ADS1299IPAG1; TQFP-64_10x10mm_P0.5mm

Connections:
+2V5: C27.1, C28.1, C31.1, C32.1, J3.2, J3.4, U7.19 (AVDD), U7.21 (AVDD), U7.22 (AVDD), U7.54 (AVDD1), U7.56 (AVDD), U7.59 (AVDD); also elsewhere on the board
+3.3V: C25.1, C26.1, J2.1, J2.2, R29.2, U7.35 (~PWDN), U7.48 (DVDD), U7.50 (DVDD)
-2V5: C17.2, C18.2, C19.2, C20.2, C21.2, C22.2, C23.2, C29.1, C30.1, C31.2, C32.2, J4.2, J4.4, U7.20 (AVSS), U7.23 (AVSS), U7.25 (VREFN), U7.32 (AVSS), U7.53 (AVSS1), U7.57 (AVSS), U7.58 (AVSS); also elsewhere on the board
/ADS1299/BIAS_INV: J3.6, R27.1, U7.61 (BiASINV)
/ADS1299/CLK: J2.12, U7.37 (CLK)
/ADS1299/CS: R18.2, R19.2, U7.39 (~CS)
/ADS1299/CS1: J2.10, R18.1
/ADS1299/CS2: J2.9, R19.1
/ADS1299/DIN: J2.14, U7.34 (DIN)
/ADS1299/DOUT: J2.6, U7.43 (DOUT)
/ADS1299/DRDY: R20.2, R21.2, U7.47 (~DRDY)
/ADS1299/DRDY1: J2.4, R20.1
/ADS1299/DRDY2: J2.3, R21.1
/ADS1299/IBIAS: R25.2, R26.2, R27.2; also elsewhere on the board
/ADS1299/IN1N: U7.15 (IN1N); also elsewhere on the board
/ADS1299/IN1P: U7.16 (IN1P); also elsewhere on the board
/ADS1299/IN2N: U7.13 (IN2N); also elsewhere on the board
/ADS1299/IN2P: U7.14 (IN2P); also elsewhere on the board
/ADS1299/IN3N: U7.11 (IN3N); also elsewhere on the board
/ADS1299/IN3P: U7.12 (IN3P); also elsewhere on the board
/ADS1299/IN4N: U7.9 (IN4N); also elsewhere on the board
/ADS1299/IN4P: U7.10 (IN4P); also elsewhere on the board
/ADS1299/IN5N: U7.7 (IN5N); also elsewhere on the board
/ADS1299/IN5P: U7.8 (IN5P); also elsewhere on the board
/ADS1299/IN6N: U7.5 (IN6N); also elsewhere on the board
/ADS1299/IN6P: U7.6 (IN6P); also elsewhere on the board
/ADS1299/IN7N: U7.3 (IN7N); also elsewhere on the board
/ADS1299/IN7P: U7.4 (IN7P); also elsewhere on the board
/ADS1299/IN8N: U7.1 (IN8N); also elsewhere on the board
/ADS1299/IN8P: U7.2 (IN8P); also elsewhere on the board
/ADS1299/ISRB1: U7.17 (SRB1); also elsewhere on the board
/ADS1299/ISRB2: U7.18 (SRB2); also elsewhere on the board
/ADS1299/RESET: J2.11, U7.36 (~RESET)
/ADS1299/SCLK: J2.8, U7.40 (SCLK)
GND: C25.2, C26.2, C27.2, C28.2, C29.2, C30.2, J2.15, J2.16, J3.1, J3.3, J3.5, J4.1, J4.3, R28.1, U7.31 (RESV1), U7.33 (DGND), U7.41 (DAISY_IN), U7.49 (DGND), U7.51 (DGND), U7.60 (BIASREF), U7.64 (RSRVD); also elsewhere on the board
unnamed: C24.2, R17.2, R26.1
unnamed: C24.1, R17.1, R25.1, U7.62 (BIASIN), U7.63 (BIASOUT)
unnamed: R28.2, R29.1, U7.52 (CLKSEL)
unnamed: C17.1, U7.28 (VCAP1)
unnamed: C18.1, U7.30 (VCAP2)
unnamed: C19.1, C20.1, U7.55 (VCAP3)
unnamed: C21.1, U7.26 (VCAP4)
unnamed: C22.1, C23.1, U7.24 (VREFP)

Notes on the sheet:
R29 fitted for clock master R28 fitted for clock slave
Select for master or slave board
Alternative Bias Circuit

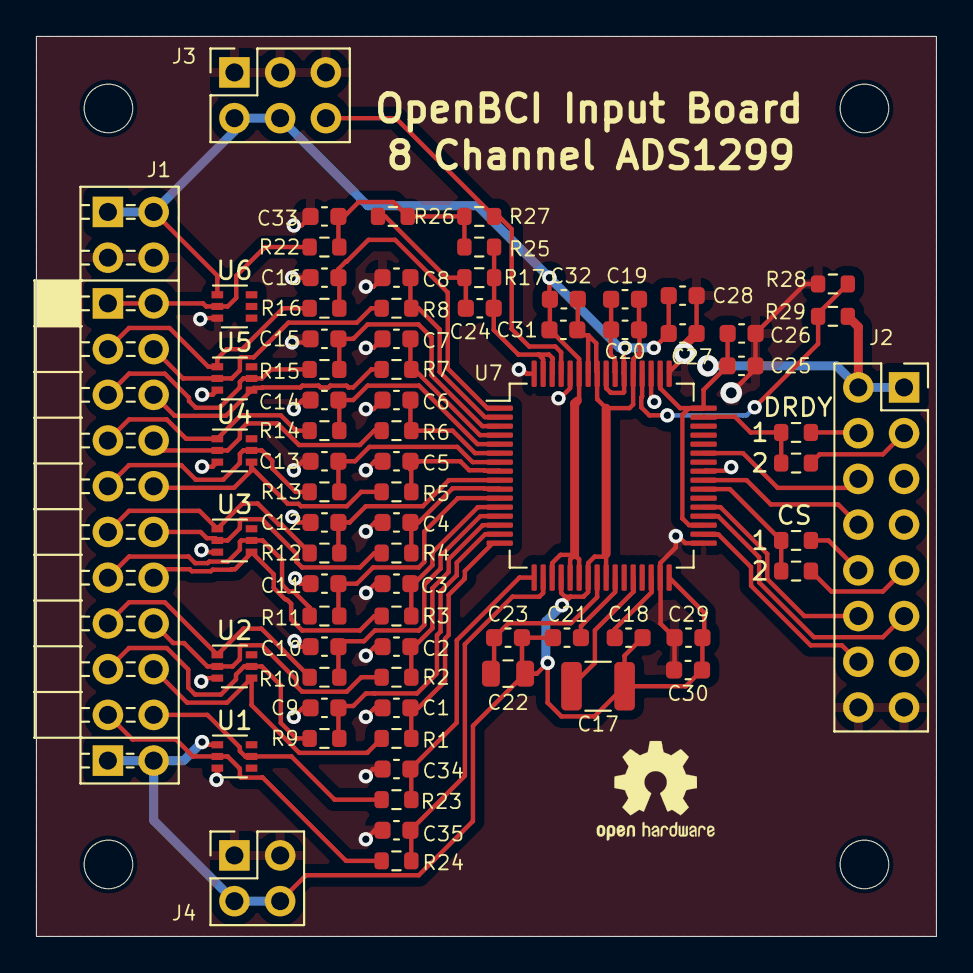
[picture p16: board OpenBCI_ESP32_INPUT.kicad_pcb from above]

Board: 2 copper layers, 50.0 x 50.0 mm, 80 parts (0 on the bottom side), 62 nets.

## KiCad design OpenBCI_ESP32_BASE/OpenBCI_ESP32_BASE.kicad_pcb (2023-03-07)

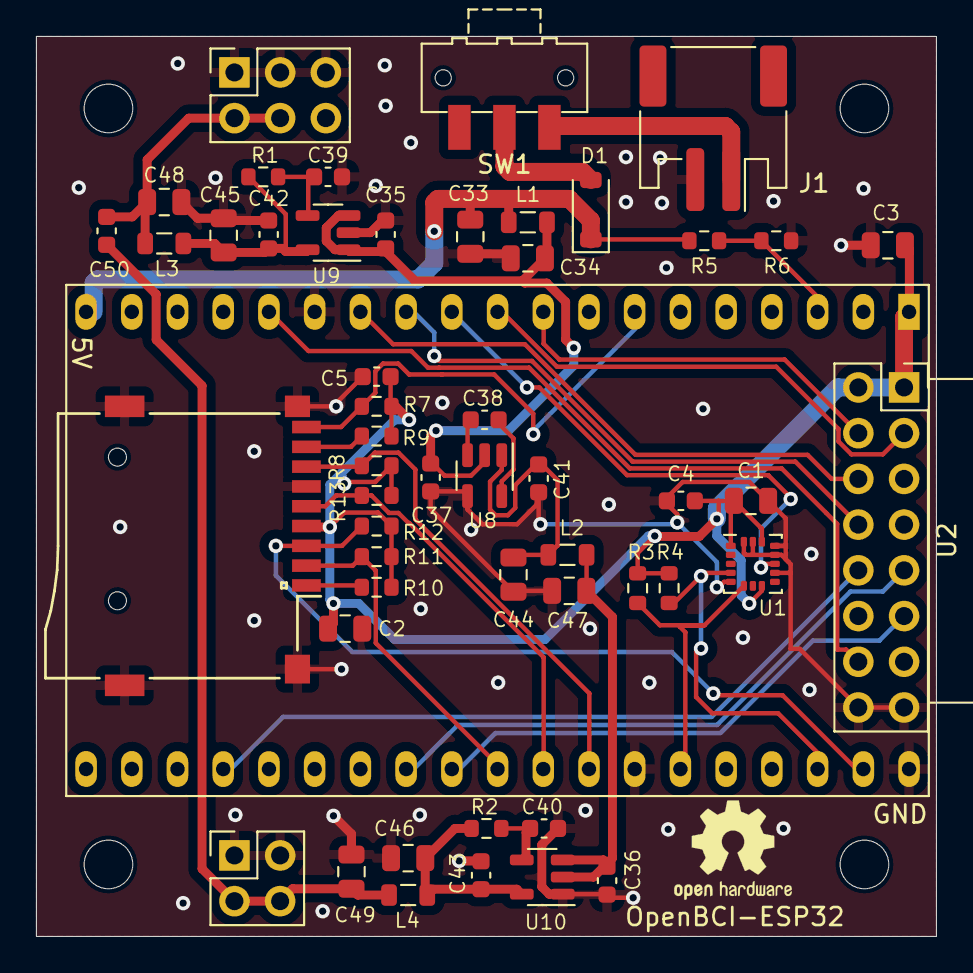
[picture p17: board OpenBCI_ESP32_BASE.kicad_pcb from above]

Board: 2 copper layers, 50.0 x 50.0 mm, 57 parts (0 on the bottom side), 33 nets.

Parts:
C1, C2, C3, C33, C34, C44, C45, C46, C47, C48, C49: 10u; C_0805_2012Metric
C4, C5, C50: 0.1u; C_0603_1608Metric
C35, C37, C38, C39, C41: 1u; C_0603_1608Metric
C36, C42, C43: 2.2u; C_0603_1608Metric
C40: 10n; C_0603_1608Metric
D1: D_Schottky; D_SOD-123
H1, H2, H3, H4: MountingHole; MountingHole_2.7mm_M2.5
J1: Conn_01x02; JST_PH_S2B-PH-SM4-TB_1x02-1MP_P2.00mm_Horizontal
J2: Conn_02x03_Odd_Even; PinHeaderReverse_2x03_P2.54mm_OpenBCI
J3: Conn_02x02_Odd_Even; PinHeaderReverse_2x02_P2.54mml_OpenBCI
J4: Conn_02x08_Odd_Even; PinHeaderReverse_2x08_P2.54mm_OpenBCI
L1, L2, L3, L4: 3.3u; L_0805_2012Metric
LOGO1: Logo_Open_Hardware_Small; OSHW-Logo2_7.3x6mm_SilkScreen
R1, R2: NF; R_0603_1608Metric
R3, R4: 4k7; R_0603_1608Metric
R5: 220k; R_0603_1608Metric
R6: 120k; R_0603_1608Metric
R7, R8, R9, R10, R11, R12, R13: 10k; R_0603_1608Metric
SW1: SW_SPDT; SW_SPDT_CK-JS102011SAQN
U1: LIS3DH; LGA-16_3x3mm_P0.5mm_LayoutBorder3x5y
U2: ESP32-DevKitC
U8: TPS60403; SOT-23-5
U9: TPS73225; SOT-23-5
U10: TPS72325; SOT-23-5
XS1: SD_ebay-uSD-push_push_SMD; Conn_uSDcard

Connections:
+2V5: C48.1, C50.1, J2.2, J2.4, L3.2
+3.3V: C1.1, C2.1, C3.1, C4.1, C5.1, J4.1, J4.2, R3.1, R4.1, R7.1, R8.1, R9.1, R10.1, R11.1, R12.1, R13.1, U1.1 (VDD_IO), U1.8 (CS), U1.14 (VDD), U2.1 (3V3), XS1.4 (Vdd)
+5V: C33.1, D1.1 (K), L1.1, R5.1, U2.19 (5V)
-2V5: C49.1, C50.2, J3.2, J3.4, L4.2
-5V: C36.1, C47.1, L2.2, U10.2 (Vin), U10.3 (EN)
/OpenBCI_ESP_DEVKIT/ADSCLK: J4.8, U2.12 (MTMS/GPIO14/ADC2_CH6)
/OpenBCI_ESP_DEVKIT/ADSCS1: J4.10, U2.23 (*MTDO/GPIO15/ADC2_CH3)
/OpenBCI_ESP_DEVKIT/ADSCS2: J4.9, U2.27 (GPIO16)
/OpenBCI_ESP_DEVKIT/ADSDRDY1: J4.4, U2.9 (DAC_1/ADC2_CH8/GPIO25)
/OpenBCI_ESP_DEVKIT/ADSDRDY2: J4.3, U2.10 (DAC_2/ADC2_CH9/GPIO26)
/OpenBCI_ESP_DEVKIT/ADSMISO: J4.6, U2.13 (*MTDI/GPIO12/ADC2_CH5)
/OpenBCI_ESP_DEVKIT/ADSMOSI: J4.14, U2.15 (MTCK/GPIO13/ADC2_CH4)
/OpenBCI_ESP_DEVKIT/ADSRST: J4.11, U2.28 (GPIO17)
/OpenBCI_ESP_DEVKIT/INT1: U1.11 (INT1), U2.11 (ADC2_CH7/GPIO27)
/OpenBCI_ESP_DEVKIT/SCL: R4.2, U1.4 (SCL/SPC), U2.36 (GPIO22)
/OpenBCI_ESP_DEVKIT/SDA: R3.2, U1.6 (SDA/SDI/SDO), U2.33 (GPIO21)
/OpenBCI_ESP_DEVKIT/SDCD: R7.2, U2.7 (32K_XP/GPIO32/ADC1_CH4), XS1.9 (CD)
/OpenBCI_ESP_DEVKIT/SDCLK: R13.2, U2.30 (GPIO18), XS1.5 (CLK)
/OpenBCI_ESP_DEVKIT/SDCS: R11.2, U2.29 (*GPIO5), XS1.2 (CS/DAT3)
/OpenBCI_ESP_DEVKIT/SDMISO: R8.2, U2.31 (GPIO19), XS1.7 (DO/DAT0)
/OpenBCI_ESP_DEVKIT/SDMOSI: R12.2, U2.37 (GPIO23), XS1.3 (DI/CMD)
GND: C1.2, C2.2, C3.2, C4.2, C5.2, C33.2, C34.2, C35.2, C36.2, C37.2, C39.2, C40.2, C41.2, C42.2, C43.2, C44.2, C45.2, C46.2, C47.2, C48.2, C49.2, J1.2, J2.1, J2.3, J2.5, J3.1, J3.3, J4.15, J4.16, R6.2, U1.5 (GND), U1.10 (GND), U1.12 (GND), U1.13 (ADC3), U1.15 (ADC2), U1.16 (ADC1), U2.14 (GND), U2.32 (GND), U2.38 (GND), U8.4 (Gnd), U9.2 (Gnd), U10.1 (Gnd), XS1.6 (GND)
unnamed: D1.2 (A), SW1.2 (B)
unnamed: J1.1, SW1.1 (A)
unnamed: R5.2, R6.1, U2.3 (SENSOR_VP/GPIO36/ADC1_CH0)
unnamed: C38.1, U8.3 (Cfly1)
unnamed: C38.2, U8.5 (Cfly2)
unnamed: C34.1, C35.1, C37.1, L1.2, U8.2 (Vin), U9.1 (Vin), U9.3 (EN)
unnamed: C41.1, C44.1, L2.1, U8.1 (Vout)
unnamed: C39.1, R1.2, U9.4 (NR)
unnamed: C42.1, C45.1, L3.1, R1.1, U9.5 (Vout)
unnamed: C40.1, R2.2, U10.4 (NR)
unnamed: C43.1, C46.1, L4.1, R2.1, U10.5 (Vout)

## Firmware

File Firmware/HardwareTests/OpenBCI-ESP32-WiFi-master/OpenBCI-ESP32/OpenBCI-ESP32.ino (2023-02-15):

#include <SPI.h>

#include <WiFi.h>
#include <WebServer.h>

#include <ESPmDNS.h>

#include <ArduinoJson.h>

#define ADS1299_PIN_RESET 17
#define ADS1299_PIN_DRDY 25

#define ADS1299_PIN_SCK 14
#define ADS1299_PIN_MISO 12
#define ADS1299_PIN_MOSI 13
#define ADS1299_PIN_SS 15

#define OPENBCI_DATA_BUFFER_SIZE 50

#define OPENBCI_NAME "OpenBCI-Axon"
#define OPENBCI_VERSION "v2.0.5"

#define SOFT_AP_SSID "OpenBCI WiFi AP"
#define SOFT_AP_PASSWORD "abcd1234*"

#define JSON_BUFFER_SIZE 1024

enum ads1299_command : uint8_t
{
    ads1299_command_start = 0x08,
    ads1299_command_stop = 0x0A,

    ads1299_command_rdatac = 0x10,
    ads1299_command_sdatac = 0x11,

    ads1299_command_rreg = 0x20,
    ads1299_command_wreg = 0x40
};

typedef struct ads1299_register_packet
{
    uint8_t id;

    uint8_t config1;
    uint8_t config2;
    uint8_t config3;

    uint8_t loff;

    uint8_t chnset[8];
    
    uint8_t bias_sensp;
    uint8_t bias_sensn;

    uint8_t loff_sensp;
    uint8_t loff_sensn;

    uint8_t loff_flip;

    uint8_t loff_statp;
    uint8_t loff_statn;

    uint8_t gpio;

    uint8_t misc1;
    uint8_t misc2;
    
    uint8_t config4;
} __attribute__ ((packed)) ads1299_register_packet;

typedef struct ads1299_data_packet
{
    uint32_t stat : 24;

    uint8_t channel_data[24];
} __attribute__ ((packed)) ads1299_data_packet;

typedef struct openbci_data_packet
{
    uint8_t header;

    uint8_t sample_number;

    uint8_t channel_data[24];

    uint8_t auxiliary_data[6];

    uint8_t footer;
} __attribute__ ((packed)) openbci_data_packet;

ads1299_register_packet ads1299_register_buffer = {};
ads1299_data_packet ads1299_data_buffer = {};

openbci_data_packet openbci_data_buffer[OPENBCI_DATA_BUFFER_SIZE] = {{}};

uint16_t openbci_data_buffer_head = 0;
uint16_t openbci_data_buffer_tail = 0;

uint8_t channel_setting_buffer[8] = {0};

uint8_t sample_counter = 0;

bool streaming_enabled = false;

uint8_t* tcp_transfer_buffer = NULL;

IPAddress local_ip(192, 168, 4, 1);
IPAddress network_gateway(192, 168, 4, 1);
IPAddress subnet_mask(255, 255, 255, 0);

WebServer web_server(80);
WiFiClient tcp_client;

size_t wifi_latency = 0;

void IRAM_ATTR ads1299_read_buffer(void* input_buffer, size_t buffer_size)
{
    spiTransferBytesNL(SPI.bus(), NULL, (uint8_t*)input_buffer, buffer_size);
}

void IRAM_ATTR ads1299_write_byte(uint8_t byte_to_write)
{
    spiWriteByteNL(SPI.bus(), byte_to_write);
}

void IRAM_ATTR ads1299_write_buffer(void* output_buffer, size_t buffer_size)
{
    spiWriteNL(SPI.bus(), (uint8_t*)output_buffer, buffer_size);
}

void ads1299_load_registers()
{
    ads1299_write_byte(ads1299_command_rreg);
    ads1299_write_byte(sizeof(ads1299_register_packet) - 1);

    ads1299_read_buffer(&ads1299_register_buffer, sizeof(ads1299_register_packet));
}

void ads1299_flush_registers()
{
    ads1299_write_byte(ads1299_command_wreg);
    ads1299_write_byte(sizeof(ads1299_register_packet) - 1);
  
    ads1299_write_buffer(&ads1299_register_buffer, sizeof(ads1299_register_packet));
}

void IRAM_ATTR ads1299_drdy_interrupt()
{
    ads1299_read_buffer(&ads1299_data_buffer, sizeof(ads1299_data_packet));
    //Serial.print(".");
    
    if (streaming_enabled)
    {
        openbci_data_buffer[openbci_data_buffer_tail].header = 0xA0;
        openbci_data_buffer[openbci_data_buffer_tail].sample_number = sample_counter++;
      
        memcpy(&openbci_data_buffer[openbci_data_buffer_tail].channel_data, &ads1299_data_buffer.channel_data, sizeof(ads1299_data_buffer.channel_data));
     
        memset(&openbci_data_buffer[openbci_data_buffer_tail].auxiliary_data, 0x00, sizeof(openbci_data_buffer[openbci_data_buffer_tail].auxiliary_data));
      
        openbci_data_buffer[openbci_data_buffer_tail].footer = 0xC0;

        if (++openbci_data_buffer_tail >= 50) openbci_data_buffer_tail = 0;
    }
}

size_t get_sampling_rate()
{
    return 16000 >> (ads1299_register_buffer.config1 & 0b111);
}

size_t get_sample_delay()
{
    return 1000000 / get_sampling_rate();
}

size_t gain_from_channel(uint8_t channel_index)
{
    uint8_t gain = (ads1299_register_buffer.chnset[channel_index] >> 4) & 0b111;
    
    switch (gain)
    {
        case 0b000:
          return 1;
        case 0b001:
          return 2;
        case 0b010:
          return 4;
        case 0b011:
          return 6;
        case 0b100:
          return 8;
        case 0b101:
          return 12;
        case 0b110:
          return 24;
        default:
          return 0;
    }
}

IPAddress ip_from_string(String ip_string)
{
    IPAddress ip_address(0, 0, 0, 0);

    ip_address.fromString(ip_string);

    return ip_address;
}

uint8_t digit_from_char(char digit_char)
{
    return digit_char - '0';
}

void get_system_info()
{
    DynamicJsonDocument json_document(JSON_BUFFER_SIZE);
    
    JsonObject json_object = json_document.to<JsonObject>();
  
    json_object["board_connected"] = true;
    json_object["heap"] = ESP.getFreeHeap();
    json_object["ip"] = WiFi.softAPIP().toString();
    json_object["latency"] = wifi_latency;
    json_object["mac"] = WiFi.softAPmacAddress();
    json_object["name"] = OPENBCI_NAME;
    json_object["num_channels"] = 8;
    json_object["version"] = OPENBCI_VERSION;
  
    String json_string = "";
  
    serializeJson(json_document, json_string);
    
    web_server.send(200, "text/json", json_string);
}

void get_board_info()
{
    DynamicJsonDocument json_document(JSON_BUFFER_SIZE);
  
    JsonObject json_object = json_document.to<JsonObject>();
  
    json_object["board_connected"] = true;
    json_object["board_type"] = "cyton";
    
    JsonArray gains = json_object.createNestedArray("gains");
  
    for (size_t channel_index = 0; channel_index < 8; channel_index++) gains.add(gain_from_channel(channel_index));

    json_object["num_channels"] = 8;
  
    String json_string = "";
  
    serializeJson(json_document, json_string);
 
    web_server.send(200, "text/json", json_string);
}

void process_command()
{    
    DynamicJsonDocument json_document(JSON_BUFFER_SIZE);
    
    deserializeJson(json_document, web_server.arg(0));
  
    JsonObject json_object = json_document.as<JsonObject>();

    String command = json_object["command"];

    String return_message = "";

    bool streaming_state = streaming_enabled;
    
    streaming_enabled = false;

    ads1299_write_byte(ads1299_command_sdatac);
  
    delayMicroseconds(50);
    
    if (command[0] == '~')
    {
        uint8_t sampling_rate = digit_from_char(command[1]);

        ads1299_register_buffer.config1 &= ~(0b111);
        ads1299_register_buffer.config1 |= sampling_rate;
        
        return_message = "Success: Sample rate is now ";
        return_message += get_sampling_rate();
        return_message += "Hz";
    }
    else if (command == "1") ads1299_register_buffer.chnset[0] = 0b10000001;
    else if (command == "2") ads1299_register_buffer.chnset[1] = 0b10000001;
    else if (command == "3") ads1299_register_buffer.chnset[2] = 0b10000001;
    else if (command == "4") ads1299_register_buffer.chnset[3] = 0b10000001;
    else if (command == "5") ads1299_register_buffer.chnset[4] = 0b10000001;
    else if (command == "6") ads1299_register_buffer.chnset[5] = 0b10000001;
    else if (command == "7") ads1299_register_buffer.chnset[6] = 0b10000001;
    else if (command == "8") ads1299_register_buffer.chnset[7] = 0b10000001;
    else if (command == "!") ads1299_register_buffer.chnset[0] = channel_setting_buffer[0];
    else if (command == "@") ads1299_register_buffer.chnset[1] = channel_setting_buffer[1];
    else if (command == "#") ads1299_register_buffer.chnset[2] = channel_setting_buffer[2];
    else if (command == "$") ads1299_register_buffer.chnset[3] = channel_setting_buffer[3];
    else if (command == "%") ads1299_register_buffer.chnset[4] = channel_setting_buffer[4];
    else if (command == "^") ads1299_register_buffer.chnset[5] = channel_setting_buffer[5];
    else if (command == "&") ads1299_register_buffer.chnset[6] = channel_setting_buffer[6];
    else if (command == "*") ads1299_register_buffer.chnset[7] = channel_setting_buffer[7];
    else if (command[0] == 'x')
    {
       uint8_t channel_index = digit_from_char(command[1]) - 1;

       uint8_t channel_power_down = digit_from_char(command[2]);
       uint8_t channel_gain = digit_from_char(command[3]);
       uint8_t channel_source = digit_from_char(command[4]);
       uint8_t channel_bias_enabled = digit_from_char(command[5]);
       uint8_t channel_srb2_enabled = digit_from_char(command[6]);
 
       uint8_t channel_setting = (channel_power_down << 7) | (channel_gain << 4) | (channel_srb2_enabled << 3) | channel_source;

       channel_setting_buffer[channel_index] = channel_setting;
       ads1299_register_buffer.chnset[channel_index] = channel_setting;

       ads1299_register_buffer.bias_sensp &= ~(1 << channel_index);
       ads1299_register_buffer.bias_sensp |= (channel_bias_enabled << channel_index);

       ads1299_register_buffer.bias_sensn &= ~(1 << channel_index);
       ads1299_register_buffer.bias_sensn |= (channel_bias_enabled << channel_index);

       uint8_t srb1_enabled = digit_from_char(command[7]);

       ads1299_register_buffer.misc1 &= ~(0b00100000);
       ads1299_register_buffer.misc1 |= (srb1_enabled << 5);
    }
    else if (command == "b") streaming_state = true;
    else if (command == "s") streaming_state = false;

    ads1299_flush_registers();
    
    ads1299_write_byte(ads1299_command_rdatac);
  
    delayMicroseconds(50);

    streaming_enabled = streaming_state;

    web_server.send(200, "text/plain", return_message);
}

void start_streaming()
{
    streaming_enabled = true;

    web_server.send(200);
}

void stop_streaming()
{
    streaming_enabled = false;

    web_server.send(200);
}

void switch_raw_output()
{
    web_server.send(200, "text/plain", "Output mode configured to raw");
}

void get_tcp_config()
{
    DynamicJsonDocument json_document(JSON_BUFFER_SIZE);
  
    JsonObject json_object = json_document.to<JsonObject>();
    
    json_object["connected"] = (tcp_client.connected() != 0) ? true : false;
    json_object["delimiter"] = false;
    json_object["ip_address"] = tcp_client.remoteIP().toString();
    json_object["output"] = "raw";
    json_object["port"] = tcp_client.remotePort();
    json_object["latency"] = wifi_latency;
  
    String json_string = "";
  
    serializeJson(json_document, json_string);

    web_server.send(200, "text/json", json_string);
}

void set_tcp_config()
{
    streaming_enabled = false;
    
    DynamicJsonDocument json_document(JSON_BUFFER_SIZE);
    
    deserializeJson(json_document, web_server.arg(0));
  
    JsonObject json_object = json_document.as<JsonObject>();
  
    String tcp_client_ip = json_object["ip"];
    wifi_latency = json_object["latency"];
    uint16_t tcp_client_port = json_object["port"];
    
    tcp_client.stop();
    
    tcp_client.connect(ip_from_string(tcp_client_ip), tcp_client_port);

    tcp_client.setNoDelay(1);
    
    get_tcp_config();
}

void stop_tcp_connection()
{
    streaming_enabled = false;
    
    tcp_client.stop();

    get_tcp_config();
}

void invalid_request()
{
    web_server.send(404, "text/plain", "Invalid Request!");
}
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

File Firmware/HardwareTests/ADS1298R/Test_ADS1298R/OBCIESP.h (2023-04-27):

/*
 OBCIESP_HW.h
 Header File with hardware definitions for OpenBCI_ESP Base board
 License: GNU General Public License V3
       
 (C) Copyright 2022 Richard Ibbotson
 */

#ifndef __OBCIESP_HW_H__
#define __OBCIESP_HW_H__

#define BOARD               DEVKIT_C

#define SERIAL_0_PORT       BTSERIAL // The primary serial Port will use the Bluetooth serial

#define SERIAL_1_PORT       ESP_SERIAL_0  // The serial debug and test port will be over the USB port
#define SERIAL_TX_PIN       3
#define SERIAL_RX_PIN       1

#define ACCEL_PORT          I2C
#define ACCEL_SDA_PIN       21
#define ACCEL_SCL_PIN       22
#define ACCEL_INT_PIN       27
#define ACCEL_I2C_ADDRESS    0x19


#define SDCARD_PORT         VSPI
#define SDCARD_MOSI_PIN     23
#define SDCARD_MISO_PIN     19
#define SDCARD_SCK_PIN      18
#define SDCARD_SSEL_PIN     5
#define SDCARD_CD_PIN       32

#define ADS129X_PORT        HSPI
#define ADS129X_MOSI_PIN    13
#define ADS129X_MISO_PIN    12
#define ADS129X_SCK_PIN     14
#define ADS129X_SSEL1_PIN   15
#define ADS129X_SSEL2_PIN   16
#define ADS129X_DRDY1_PIN   25
#define ADS129X_DRDY2_PIN   26
#define ADS129X_RESET_PIN   17
#define ADS129X_RESET_PULSE 1
#define ADS129X_RESET_DELAY 1

#define BATT_PORT       ADC1_CH0  // Measure 5V Rail
#define BATT_PIN        36    // via 220k/120k divifder
#define BATT_MAX        (3.3 * (220 + 120)/120)

#endif // __OBCIESP_HW_H__

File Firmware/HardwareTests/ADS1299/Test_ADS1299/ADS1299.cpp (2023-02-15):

/*
 LIS3DH.cpp
 Library File for LIS3DH Accelerometer for OpenBCI_ESP Base board
 License: GNU General Public License V3
       
 (C) Copyright 2022 Richard Ibbotson
 */
#include "OBCIESP.h"
#include "ADS1299.h"
#include <SPI.h>

SPIClass SPI2(HSPI);

ADS1299::ADS1299(void)
{
  
}

void ADS1299::begin()
{
  pinMode( ADS1299_RESET_PIN, OUTPUT);
  digitalWrite( ADS1299_RESET_PIN, HIGH); //set the ADS1299 reset high
  pinMode( ADS1299_SSEL1_PIN, OUTPUT);
  pinMode( ADS1299_SSEL2_PIN, OUTPUT);
  
  csHigh(ADS_1);
  csHigh(ADS_2);
  
  SPI2.begin(ADS1299_SCK_PIN, ADS1299_MISO_PIN, ADS1299_MOSI_PIN, ADS1299_SSEL1_PIN); // sck, miso, mosi, ss (ss can be any GPIO)
 
  // defines SPI comunication type and initializes module
  SPI2.beginTransaction(SPISettings(1000000, MSBFIRST, SPI_MODE1)); // SPI setup SPI communication
  delay(200); // SPI delay for initialization
  hw_reset();
 
  RESET(ADS_1); // send reset command
  RESET(ADS_2);
  SDATAC(ADS_1);  // stop continuous mode
  SDATAC(ADS_2);
  
}

void ADS1299::hw_reset()  // Hardware Reset"
{
 digitalWrite( ADS1299_RESET_PIN, LOW);
 delay(ADS1299_RESET_PULSE);
 digitalWrite( ADS1299_RESET_PIN , HIGH);
 delay(ADS1299_RESET_DELAY); 
 }


//SPI communication method
byte ADS1299::xfer(byte _data)
{
  byte inByte;
  inByte = SPI2.transfer(_data);
  return inByte;
}

//SPI chip select method
void ADS1299::csLow(int16_t SS)
{ // select an SPI slave to talk to
  switch (SS)
  {
  case ADS_1:
    digitalWrite(ADS1299_SSEL1_PIN, LOW);
    break;
  case ADS_2:
    digitalWrite(ADS1299_SSEL2_PIN, LOW);
    break;
  
  case BOTH_ADS:
    
    digitalWrite(ADS1299_SSEL1_PIN, LOW);
    digitalWrite(ADS1299_SSEL2_PIN, LOW);
    break;
  default:
    break;
  }
}

void ADS1299::csHigh(int16_t SS)
{ // deselect SPI slave
  delayMicroseconds(4);
  switch (SS)
  {
  case ADS_1:
    digitalWrite(ADS1299_SSEL1_PIN, HIGH);
    break;
  case ADS_2:
    digitalWrite(ADS1299_SSEL2_PIN, HIGH);
    break;
  case BOTH_ADS:
    digitalWrite(ADS1299_SSEL1_PIN, HIGH);
    digitalWrite(ADS1299_SSEL2_PIN, HIGH);
    break;
  default:
    break;
  }
}

uint8_t ADS1299::ADS_getDeviceID(int16_t targetSS)
{ // simple hello world com check
  uint8_t data = RREG(ID_REG, targetSS);
  return data;
}
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

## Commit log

2021-12-02 Add Kicad files
    [ADS1299.sch, Analog_Input.sch, JS102011SAQN.STEP, OpenBCI_ESP32_BASE.kicad_pcb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]
2021-12-03 Add ESP32 Devkit image
2021-12-03 Update Input Board Silk Screen
    [ADS1299.sch, OpenBCI_ESP32_INPUT.kicad_pcb]
2022-01-26 Latest PCB file and firmware
    [ADS1299.kicad_sch, Analog_Input.kicad_sch, OpenBCI_ESP32_BASE-B_Cu.gbr, OpenBCI_ESP32_BASE-B_Mask.gbr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]
2022-01-30 Add Fusion 360 and STL for case
    [Base.stl, Battery.stl, Input_8.stl, OpenBCI_ESP v11.f3d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]
2022-01-31 Firmware updates
    [OpenBCI_ESP32_BASE.csv, OpenBCI_ESP32_BASE.kicad_pcb, OpenBCI_ESP32_BASE.kicad_sch, OpenBCI_ESP32_INPUT.csv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]
2022-02-01 Kicad and firmware updates
    Kicad schematic and PCB updates for SD Card issue
    Firmware tests for SD card
    [OpenBCI_ESP32_BASE.kicad_pcb, OpenBCI_ESP32_BASE.kicad_sch, OpenBCI_ESP_DEVKIT.kicad_sch, Power Supplies.kicad_sch]
2023-02-15 Code and STL updates
    [ADS1299.kicad_sch, Base.stl, Battery.stl, OpenBCI_ESP32_BASE-B_Cu.gbr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]
2023-03-07 add ADS1298 files
    [ADS1298.kicad_sch, Analog_Input.kicad_sch, OpenBCI_ESP32_ADS1298.kicad_pcb, OpenBCI_ESP32_ADS1298.kicad_sch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]
2023-03-07 Update footprints
    [ADS1298.kicad_sch, Analog_Input.kicad_sch, OpenBCI_ESP32_ADS1298.kicad_pcb, OpenBCI_ESP32_INPUT.kicad_pcb]
2023-03-08 Changes to meet JLCPCB Rules
    Change BGA pad size and track routing. Change Via size to lower cost
    [ADS1298.kicad_sch, OpenBCI_ESP32_ADS1298-B_Cu.gbr, OpenBCI_ESP32_ADS1298-B_Mask.gbr, OpenBCI_ESP32_ADS1298-B_Paste.gbr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]
2023-04-27 Fix ADS1298 Mounting Holes
    Fix ADS1298R Mounting holes shorting layers
    Add some ADS1298R Arduino Files
    [Analog_Input.kicad_sch, OpenBCI_ESP32_ADS1298-B_Cu.gbr, OpenBCI_ESP32_ADS1298-B_Mask.gbr, OpenBCI_ESP32_ADS1298-B_Paste.gbr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]
